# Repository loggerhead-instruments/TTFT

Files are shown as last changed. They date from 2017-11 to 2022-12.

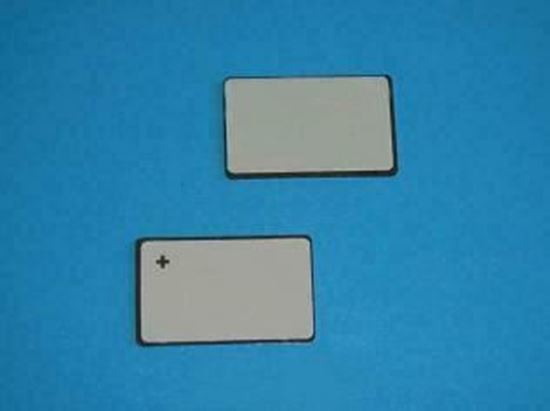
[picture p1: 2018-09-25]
spec_sheets/piezoAmp/Piezoelectric Ceramic Plate Transducer 190 KHz - SMPL131W89T10 - STEMINC_files/0001703_piezo-ceramic-plate-131x89x1mm-190-khz_550.jpeg

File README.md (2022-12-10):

# TTFT
Teeny tiny fish accelerometer tag

TTFT are miniature high-speed acceleromter data logger tags

## Altium
0. TTFT: AtMega328p high-speed accelerometer tag running at 3.0V. No real-time clock.
1. TTFT_3.0: AtMega328p development board designed to run at 3.0V
2. TTFT_3.0_tiny: AtMega328p high-speed accelerometer tag running at 3.0V. No real-time clock. No crystal for AtMega328p (to make smaller).
3. TTFT_1.8: AtMega328p high-speed accelerometer tag with 1.8V regulator to run accelerometer at lower voltage. No real-time clock.
4. TTFT2: ATSAMD21GA high-speed accelerometer tag with real-time clock. Supports MS5837 depth and temperature sensor. Magnetic switch.
5. TTFT3: ATSAMD21GA high-speed accelerometer tag with real-time clock. Supports MS5837 depth and temperature sensor. Magnetic switch. Adds pinger circuit.

## Arduino
Firmware for TTFT tags

## spec_sheets
Technical specification sheets for TTFT tag components.

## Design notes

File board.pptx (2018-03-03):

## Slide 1

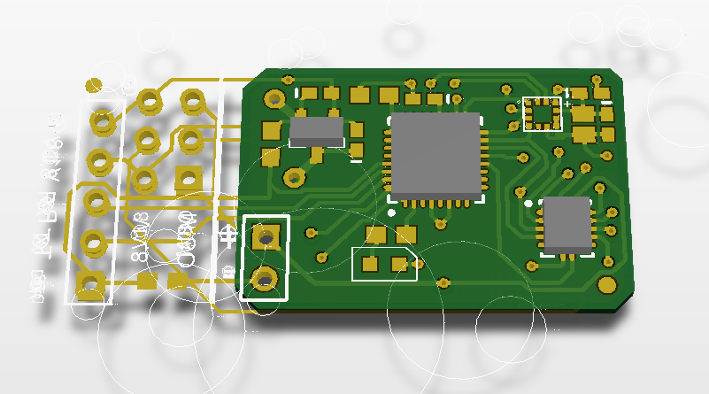
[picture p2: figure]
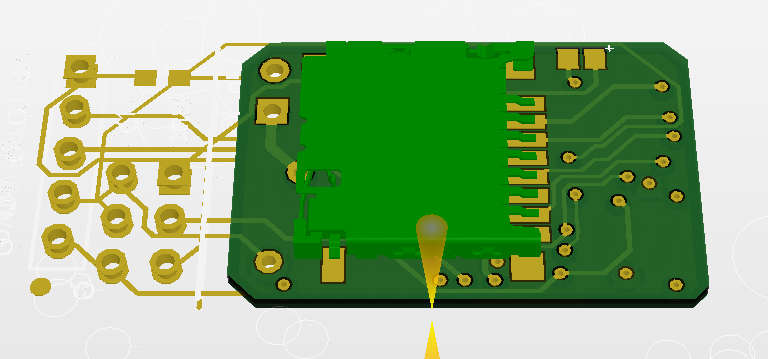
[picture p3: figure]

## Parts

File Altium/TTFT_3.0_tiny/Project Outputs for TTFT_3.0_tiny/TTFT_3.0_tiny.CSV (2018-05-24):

Bill of Material for
On 5/22/2018 at 4:47:26 PM
Comment | Manufacturer | Part number | DigiKey part number | Pattern | Quantity | Components
0.1uF | Any |  |  | 402 | 1 | C3 | Ceramic Chip Capacitor - Standard
1.0uF | Any |  |  | 402 | 2 | C8, C9 | Ceramic Chip Capacitor - Standard
100nF | Any |  |  | 402 | 2 | C5, C7 | Ceramic Chip Capacitor - Standard
10k | Any |  |  | 3-0603 | 1 | R1 | Precision Thick Film Chip Resistor, 10 Ohm to 1M Ohm Range, 1% and 0.5% Tolerance, 0603 Size, 0.063 W
10uF | Any |  |  | 805 | 1 | C6 | Tantalum cap
330x | Any |  |  | 3-0603 | 1 | R3 | Precision Thick Film Chip Resistor, 10 Ohm to 1M Ohm Range, 1% and 0.5% Tolerance, 0603 Size, 0.063 W
ATmega328P-MU | Microchip | ATmega328P-MU | ATMEGA328PB-MU-ND | 32M1-A_M | 1 | U1 | 8-Bit AVR Microcontroller with 8K Bytes of In-System Programmable Flash Memory
red LED_0603 | Any |  | SML-D12V1WT86TR-ND | Diode0603 | 1 | D1
Level Shifter | NXP | NTB0104BQ,115 | 568-8404-1-ND | DHVQFN14 | 2 | U3, U5 | Voltage level translator
LIS2DS12 | STMicroelectronics | LIS2DS12TR | 497-16261-1-ND | LGA-12 | 1 | U2
1.8V LDO | Microchip | MCP1700T-1802E/TT | MCP1700T1802ETTTR-ND | SOT-23-TT3_N | 1 | U4 | Low Quiescent Current LDO, 3-Pin SOT-23, Extended Temperature, Tape and Reel
microSD Hirose push-pull | Hirose | DM3D-SF | HR1941DKR-ND | DM3D microSD | 1 | P4

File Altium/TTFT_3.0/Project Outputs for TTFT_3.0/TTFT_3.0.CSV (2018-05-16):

Bill of Material for
On 5/14/2018 at 1:20:30 PM
Comment | Pattern | Quantity | Components
0.1uF | 0402 | 1 | C3 | Ceramic Chip Capacitor - Standard
1.0uF | 0402 | 2 | C8, C9 | Ceramic Chip Capacitor - Standard
100nF | 0402 | 2 | C5, C7 | Ceramic Chip Capacitor - Standard
10k | 3-0603 | 1 | R1 | Precision Thick Film Chip Resistor, 10 Ohm to 1M Ohm Range, 1% and 0.5% Tolerance, 0603 Size, 0.063 W
10uF | Tant0805 | 2 | C4, C6
330 | 3-0603 | 1 | R3 | Precision Thick Film Chip Resistor, 10 Ohm to 1M Ohm Range, 1% and 0.5% Tolerance, 0603 Size, 0.063 W
ATmega8-16AC | 32M1-A_M | 1 | U1 | 8-Bit AVR Microcontroller with 8K Bytes of In-System Programmable Flash Memory
AVR SPI | HDR2X3 | 1 | P3 | Header, 3-Pin, Dual row
CoinCellHolder | CoinCellHolder | 1 | P24
Header 2 | HDR1X2 | 1 | P5 | Header, 2-Pin
Header 5 | HDR1X5 | 1 | P2 | Header, 5-Pin
Header 8X2A | HDR2X8_CEN | 1 | P1 | Header, 8-Pin, Dual row
LED_0603 | Diode0603 | 1 | D1
Level Shifter | DHVQFN14 | 2 | U3, U5 | Voltage level translator
LIS2DS12 | LGA-12 | 1 | U2
MCP1700T-1802E/TT | SOT-23-TT3_N | 1 | U4 | Low Quiescent Current LDO, 3-Pin SOT-23, Extended Temperature, Tape and Reel
microSD Hirose | DM3D microSD | 1 | P4
omit | 3-0603 | 2 | R2, R4 | Precision Thick Film Chip Resistor, 10 Ohm to 1M Ohm Range, 1% and 0.5% Tolerance, 0603 Size, 0.063 W

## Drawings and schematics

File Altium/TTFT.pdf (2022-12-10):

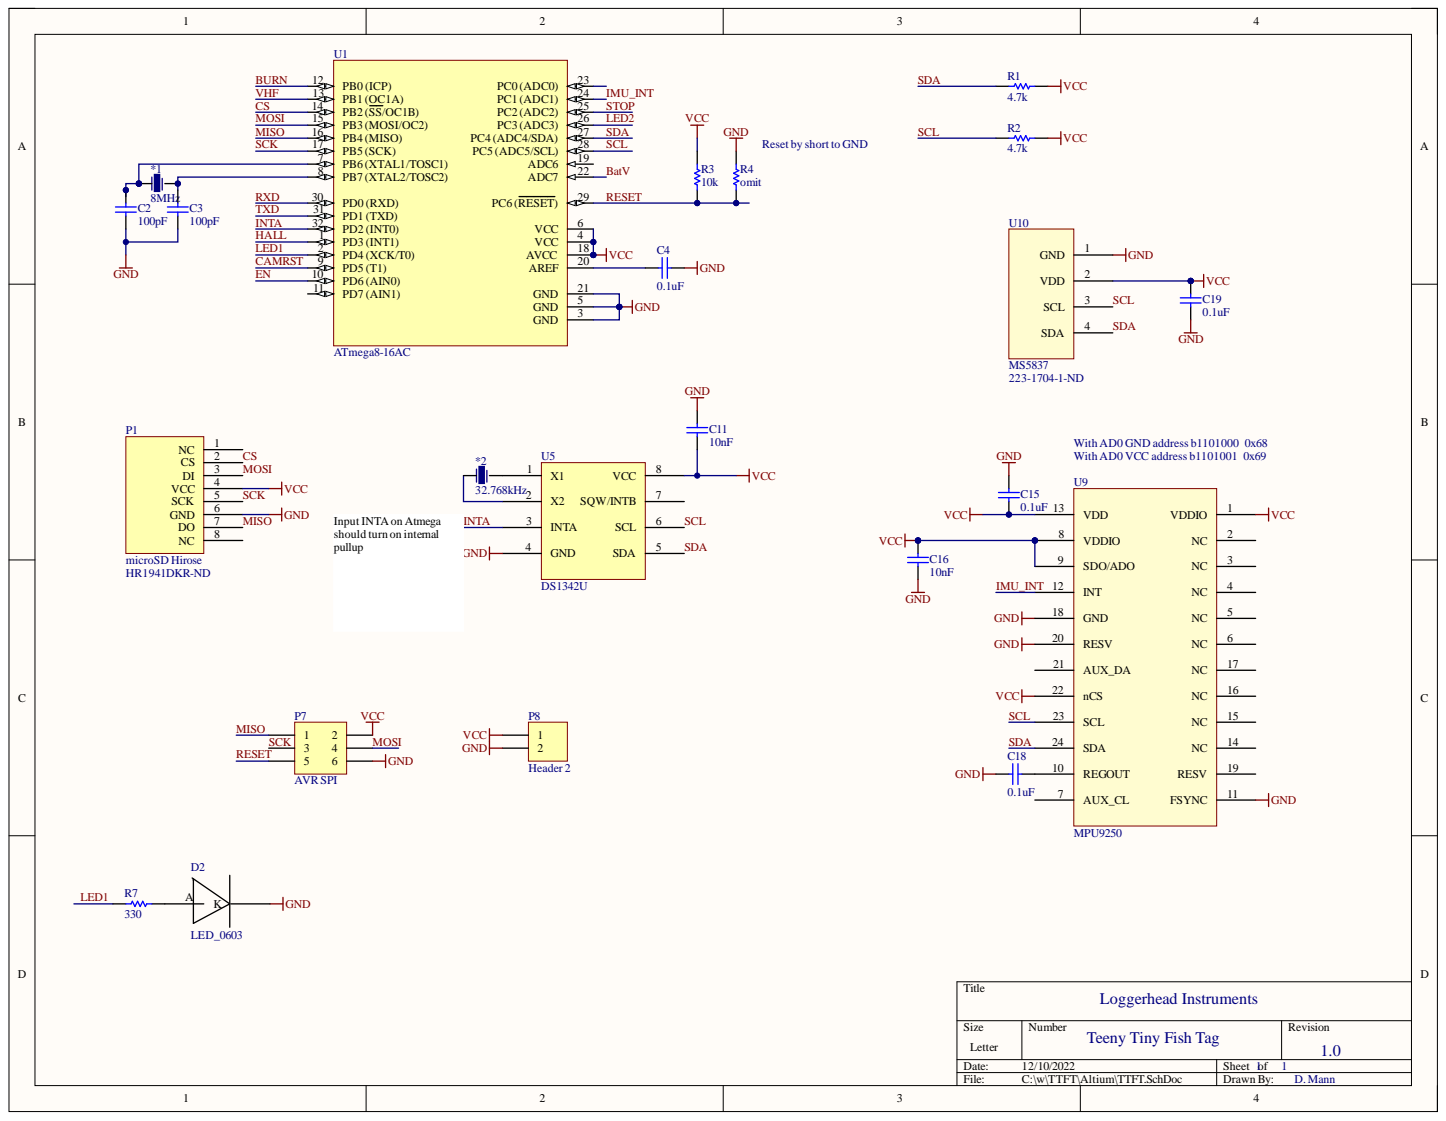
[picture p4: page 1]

Reset by short to GND

InputINTAon Atmega
should turn on internal
pullup

Teeny Tiny Fish Tag

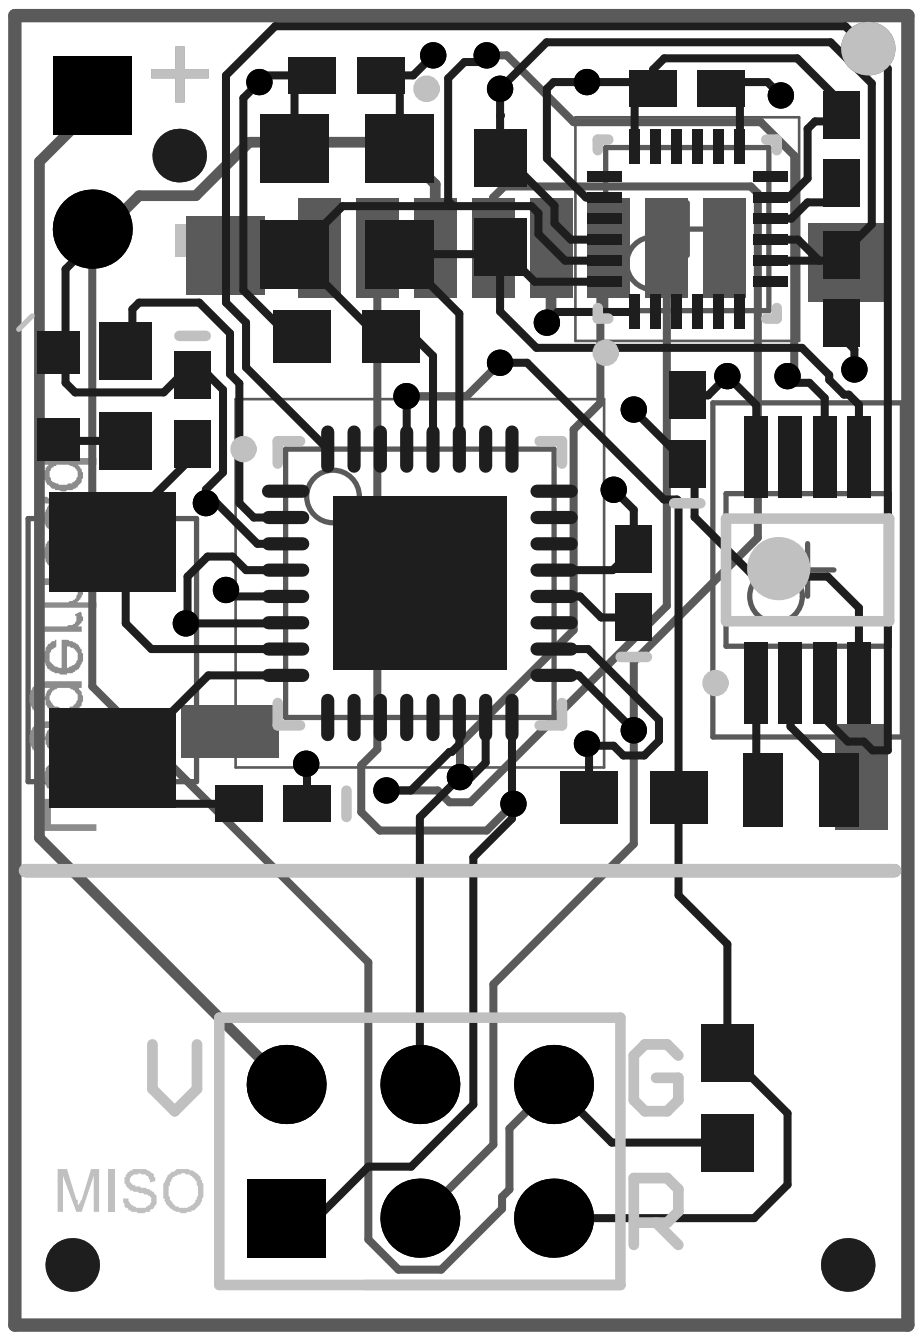
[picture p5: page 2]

Comment | Description | Designator | Footprint | LibRef | Quantity
8MHz | | *1 | XTAL-ABM3 | XTAL-ABM3 | 1
32.768kHz | | *2 | XTAL-ABS06 | XTAL_ABS06 | 1
100pF | Ceramic Chip Capacitor - Standard | C2, C3 | 0402 | C0402 | 2
0.1uF | Ceramic Chip Capacitor - Standard | C4, C15, C18, C19 | 0402 | C0402 | 4
10nF | Ceramic Chip Capacitor - Standard | C11, C16 | 0402 | C0402 | 2
LED_0603 | | D2 | Diode0603 | LED_0603 | 1
microSD Hirose | | P1 | DM3D microSD | microSD Hirose | 1
AVR SPI | Header, 3-Pin, Dual row | P7 | HDR2X3 | Header 3X2 | 1
Header 2 | Header, 2-Pin | P8 | HDR1X2 | Header 2 | 1
4.7k | Precision Thick Film Chip Resistor, 10 Ohm to 1M Ohm Range, 1% and 0.5% Tolerance, 0603 Size, 0.063 W | R1, R2 | 3-0603 | ERJ3RK | 2
10k | Precision Thick Film Chip Resistor, 10 Ohm to 1M Ohm Range, 1% and 0.5% Tolerance, 0603 Size, 0.063 W | R3 | 3-0603 | ERJ3RK | 1
omit | Precision Thick Film Chip Resistor, 10 Ohm to 1M Ohm Range, 1% and 0.5% Tolerance, 0603 Size, 0.063 W | R4 | 3-0603 | ERJ3RK | 1
330 | Precision Thick Film Chip Resistor, 10 Ohm to 1M Ohm Range, 1% and 0.5% Tolerance, 0603 Size, 0.063 W | R7 | 3-0603 | ERJ3RK | 1
ATmega8-16AC | 8-Bit AVR Microcontroller with 8K Bytes of In-System Programmable Flash Memory | U1 | 32M1-A_M | ATmega8-16AC | 1
DS1342U | | U5 | uSOP8 | DS1337 | 1
MPU9250 | Invensense | U9 | MPU6500 | MPU-9250 | 1
MS5837 | Pressure/Temp | U10 | MS5837 | MS5837 | 1

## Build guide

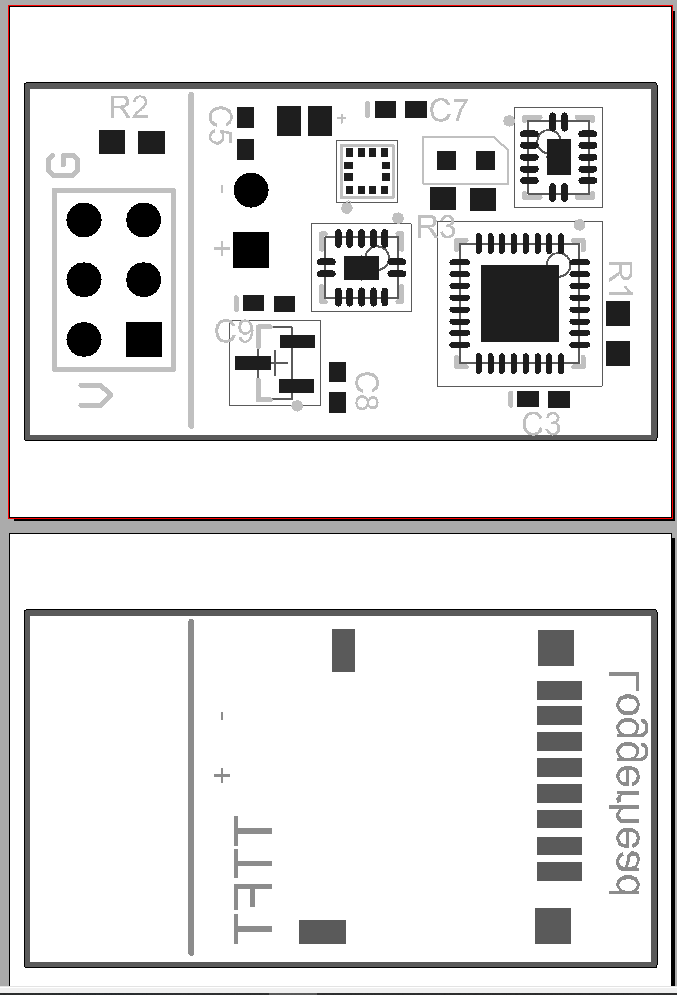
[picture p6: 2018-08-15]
Altium/TTFT_3.0_tiny/Project Outputs for TTFT_3.0_tiny/TTFT_3.0_tiny_assembly.PNG

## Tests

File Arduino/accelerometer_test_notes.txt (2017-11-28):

MPU9250
Have to use either 1000 Hz (too low) or 4000 Hz with all 3 accelerometer axes with FIFO.
No watermark

Results: Can't keep up with downloading over I2C

LIS2DS12
Has magnitude mode
256-level FIFO
14-bit
1600, 3200, 6400 Hz
If using magnitude mode, still only get 256 samples because I think it uses 3 per time slot.
watermark
Operates at a lower voltage than microSD card
150 uA at 1.8V

KX126-1063
2048-byte buffer
8 or 16-bit resolution (683 sets at low res; 342 sets at high res)
1600, 3200, 6400, 12800, 25600 data rates
watermark
145 uA at 2.5V
Confusing: Spec sheet says "Additional data can not be written to the buffer while data is being read from the buffer using auto-increment mode."
But, bullet points say can read buffer while it is being written to

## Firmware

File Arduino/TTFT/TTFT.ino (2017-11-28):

// Copyright Loggerhead Instruments, 2017
// David Mann

// TTFT is an underwater motion datalogger
// designed around the ATMEGA328p


/*
 *  RTC trigger interrupt once per second
 *  read FIFO buffer and write it
 *  check for errors on sensor init
 */


//#include <Wire.h>
#include <SPI.h>
#include <SdFat.h>
#include <MsTimer2.h> 
#include <avr/sleep.h>
#include <avr/power.h>
#include <prescaler.h>

#define SDA_PORT PORTC
#define SDA_PIN 4
#define SCL_PORT PORTC
#define SCL_PIN 5

#define I2C_TIMEOUT 100
#define I2C_FASTMODE 1

#include <SoftWire.h>
#include <avr/io.h>
#include <avr/boot.h>

SoftWire Wire = SoftWire();

//
// DEV SETTINGS
//
float codeVer = 1.00;
int printDiags = 1;

int recDur = 300;
int recInt = 0;
int LED_EN = 1; //enable green LEDs flash 1x per pressure read. Can be disabled from script.

#define MS5837_02bar // Pressure sensor. Each sensor has different constants.

#ifdef MS5837_02bar
  #define MS58xx_constant 327680.0
  #define pressAddress 0x76
#endif
#ifdef MS5837_30bar
  #define MS58xx_constant 8192.0
  #define pressAddress 0x76
#endif

// pin assignments
#define chipSelect  10
#define LED_GRN A3  // PD4
#define BURN 8     // PB0
#define VHFPOW 9   // PB1
#define BUTTON1 A2 // PC2
#define BAT_VOLTAGE A7// ADC7
#define HALL 3 // PD3 (INT1)

// SD file system
SdFat sd;
File dataFile;
int fileCount; 

int ssCounter; // used to get different sample rates from one timer based on imu_srate
byte clockprescaler=0;  //clock prescaler

//
// SENSORS
//
byte imuTempBuffer[64];
int imuSrate = 50; // must be integer for timer
int sensorSrate = 1; // must divide into imuSrate
int slowRateMultiple = imuSrate / sensorSrate;
int speriod = 1000 / imuSrate;

//Pressure and temp calibration coefficients
uint16_t PSENS; //pressure sensitivity
uint16_t POFF;  //Pressure offset
uint16_t TCSENS; //Temp coefficient of pressure sensitivity
uint16_t TCOFF; //Temp coefficient of pressure offset
uint16_t TREF;  //Ref temperature
uint16_t TEMPSENS; //Temperature sensitivity coefficient
byte Tbuff[3];
byte Pbuff[3];
volatile float depth, temperature, pressure_mbar;
boolean togglePress = 0; // flag to toggle conversion of temperature and pressure

// RGB
int16_t islRed;
int16_t islBlue;
int16_t islGreen;
int16_t accelX, accelY, accelZ;
int16_t magX, magY, magZ;
int16_t gyroX, gyroY, gyroZ;

int accel_scale = 16;

// impeller spin counter
volatile int spin;

// System Modes and Status
int mode = 0; //standby = 0; running = 1
volatile float voltage;

// Time
volatile byte second = 0;
volatile byte minute = 0;
volatile byte hour = 17;
volatile byte day = 1;
volatile byte month = 1;
volatile byte year = 17;

unsigned long t, startTime, endTime, burnTime;
int burnFlag = 0;
long burnSeconds;

void setup() {
  Serial.begin(115200);
  pinMode(LED_GRN, OUTPUT);
  pinMode(BUTTON1, INPUT_PULLUP);
  pinMode(BAT_VOLTAGE, INPUT);
  
  digitalWrite(LED_GRN,HIGH);
  pinMode(2, INPUT); //Arduino Interrupt2
  pinMode(3, INPUT); //Arduino Interrupt1

  Serial.println("TTFT");
  Wire.begin();
  
  Serial.println("Init microSD");
  // see if the card is present and can be initialized:
  while (!sd.begin(chipSelect, SPI_FULL_SPEED)) {
    Serial.println("Card failed");
    digitalWrite(LED_GRN, HIGH);
    delay(200);
    digitalWrite(LED_GRN, LOW);
    delay(100);
  }
  loadScript(); // do this early to set time
  initSensors();
  readRTC();
  Serial.print(year); Serial.print(" ");
 Serial.print(month);Serial.print(" ");
 Serial.print(day);Serial.print(" ");
 Serial.print(hour);Serial.print(" ");
 Serial.print(minute);Serial.print(" ");
 Serial.print(second);

 logFileWrite();
  
  if(burnFlag==2){
    burnTime = t + burnSeconds;
    Serial.print("Burn time set");
    Serial.println(burnTime);
  }
  if(startTime==0) startTime = t + 0; 
  Serial.print("Time:"); Serial.println(t);
  Serial.print("Start Time:"); Serial.println(startTime);
  digitalWrite(LED_GRN, LOW);

  setClockPrescaler(clockprescaler); // set clockprescaler from script file

  //setupWDT(11); // initialize and activate WDT with maximum period (~500 ms)

}

void loop() {
  while(mode==0){
    readRTC();
    Serial.print(t); Serial.print(" "); Serial.println(startTime);
    delay(1000);
    if(t >= startTime){
      endTime = startTime + recDur;
      startTime += recDur + recInt;  // this will be next start time for interval record
      fileInit();
      updateTemp();  // get first reading ready
      mode = 1;
      resetGyroFIFO();
      startInterruptTimer(1, clockprescaler);
    }
  } // mode = 0


  while(mode==1){
    // check if time to close
    if(t>=endTime){
      dataFile.close(); // close file
      if(recInt==0){  // no interval between files
        endTime += recDur;  // update end time
        fileInit();
        break;
      }
      mode = 0;
      break;
    }

    // Check if stop button pressed
    if(digitalRead(BUTTON1)==0){
      delay(10); // simple deBounce
      if(digitalRead(BUTTON1)==0){
        stopTimer();
        digitalWrite(LED_GRN, HIGH);
        dataFile.close();
        delay(30000);
        // wait 30 s to stop
        startInterruptTimer(speriod, clockprescaler);
        fileInit();
        digitalWrite(LED_GRN, LOW);
      }
    }
  } // mode = 1
  
}


void initSensors(){
// Battery Voltage
  for(int x = 0; x<10; x++){
    readVoltage();
   // Serial.println(voltage);
    delay(100);
  }

  reset_alarm();
//  Serial.println(rtcStatus());
//  for(int i=0; i<10; i++){
//    readRTC();
//    Serial.println(second);
//    delay(1000);
//  }
  // flash LED with current hour
  digitalWrite(LED_GRN, LOW);
  delay(1000);
  readRTC();
  for(int i=0; i<hour; i++){
    delay(300);
    digitalWrite(LED_GRN, HIGH);
    delay(100);
    digitalWrite(LED_GRN, LOW);
  }


  // Pressure/Temperature
  pressInit();
  for(int x=0; x<10; x++){
    updatePress();
    delay(100);
    readPress();
    updateTemp();
    delay(100);
    readTemp();
    calcPressTemp();
//    Serial.print(" press:"); Serial.print(pressure_mbar);
//    Serial.print(" depth:"); Serial.print(depth);
//    Serial.print(" temp:"); Serial.println(temperature);
  }
  
  mpuInit(1);
//  for(int i=0; i<30; i++){
//      readImu();
//      calcImu();
//      printImu();
//      delay(100);
//    }
}

void calcImu(){
      accelX = (int16_t) ((int16_t)imuTempBuffer[0] << 8 | imuTempBuffer[1]);    
      accelY = (int16_t) ((int16_t)imuTempBuffer[2] << 8 | imuTempBuffer[3]);   
      accelZ = (int16_t) ((int16_t)imuTempBuffer[4] << 8 | imuTempBuffer[5]);    
      
     // gyroTemp = (int16_t) (((int16_t)imuTempBuffer[6]) << 8 | imuTempBuffer[7]);   
     
      gyroX = (int16_t)  (((int16_t)imuTempBuffer[8] << 8) | imuTempBuffer[9]);   
      gyroY = (int16_t)  (((int16_t)imuTempBuffer[10] << 8) | imuTempBuffer[11]); 
      gyroZ = (int16_t)  (((int16_t)imuTempBuffer[12] << 8) | imuTempBuffer[13]);   
      
      magX = (int16_t)  (((int16_t)imuTempBuffer[14] << 8) | imuTempBuffer[15]);   
      magY = (int16_t)  (((int16_t)imuTempBuffer[16] << 8) | imuTempBuffer[17]);   
      magZ = (int16_t)  (((int16_t)imuTempBuffer[18] << 8) | imuTempBuffer[19]);  
}

void printImu(){
      Serial.print("a/m/g:\t");
      Serial.print(accelX); Serial.print("\t");
      Serial.print(accelY); Serial.print("\t");
      Serial.print(accelZ); Serial.print("\t");
      Serial.print(magX); Serial.print("\t");
      Serial.print(magY); Serial.print("\t");
      Serial.print(magZ); Serial.print("\t");
      Serial.print(gyroX); Serial.print("\t");
      Serial.print(gyroY); Serial.print("\t");
      Serial.println(gyroZ);
}

void fileWriteImu(){
  dataFile.print(accelX); dataFile.print(",");
  dataFile.print(accelY); dataFile.print(",");
  dataFile.print(accelZ); dataFile.print(",");
  dataFile.print(magX); dataFile.print(",");
  dataFile.print(magY); dataFile.print(",");
  dataFile.print(magZ); dataFile.print(",");
  dataFile.print(gyroX); dataFile.print(",");
  dataFile.print(gyroY); dataFile.print(",");
  dataFile.print(gyroZ);
}

void fileWriteImuFifo(){
  
}

void fileWriteSlowSensors(){
   dataFile.print(','); dataFile.print(year);  
    dataFile.print('-');
    if(month < 10) dataFile.print('0');
    dataFile.print(month);
    dataFile.print('-');
    if(day < 10) dataFile.print('0');
    dataFile.print(day);
    dataFile.print('T');
    if(hour) dataFile.print('0');
    dataFile.print(hour);
    dataFile.print(':');
   if(minute < 10) dataFile.print('0');
   dataFile.print(minute);
   dataFile.print(':');
   if(second < 10) dataFile.print('0');
   dataFile.print(second);
   dataFile.print("Z,");
    dataFile.print(','); dataFile.print(pressure_mbar);
    dataFile.print(','); dataFile.print(depth);
    dataFile.print(','); dataFile.print(temperature);
    dataFile.print(','); dataFile.print(voltage);
}

void logFileWrite()
{
   readRTC();
   
   File logFile = sd.open("log.txt", O_WRITE | O_CREAT | O_APPEND);
   logFile.print("Code version:"); logFile.println(codeVer);
   logFile.print("Serial Number: ");
   for (uint8_t i = 14; i < 24; i += 1) {
       logFile.print(boot_signature_byte_get(i), HEX);
   }
   logFile.println();
   logFile.print(year);  logFile.print("-");
   logFile.print(month); logFile.print("-");
   logFile.print(day); logFile.print("T");
   logFile.print(hour); logFile.print(":");
   logFile.print(minute); logFile.print(":");
   logFile.println(second);

   logFile.close();
}


void flatFileOpen()
{
   readRTC();
   
   dataFile = sd.open("flat.csv", O_WRITE | O_CREAT);
   dataFile.println("accelX,accelY,accelZ,magX,magY,magZ");
   SdFile::dateTimeCallback(file_date_time);
}

void fileInit()
{
   char filename[60];
   sprintf(filename,"%02d%02d%02dT%02d%02d%02d.csv", year, month, day, hour, minute, second);  //filename is DDHHMM
   dataFile = sd.open(filename, O_WRITE | O_CREAT | O_APPEND);
   while (!dataFile){
    fileCount += 1;
    sprintf(filename,"F%06d.amx",fileCount); //if can't open just use count
    dataFile = sd.open(filename, O_WRITE | O_CREAT | O_EXCL);
   // Serial.println(filename);
    delay(100);
   }
   dataFile.println("accelX,accelY,accelZ,magX,magY,magZ,gyroX,gyroY,gyroZ,date,red,green,blue,mBar,depth,temperature,spin,V");
   SdFile::dateTimeCallback(file_date_time);
   Serial.println(filename);
}

/********************************************************************
***        Master Interrupt Routine to Read Sensors               ***
********************************************************************/
void sampleSensors(void){  
    if(LED_EN) digitalWrite(LED_GRN, HIGH);
    int fifoPts = getImuFifoPts();
    
    if(fifoPts>64){
      Serial.println(fifoPts);
      readImuFifo(64);
    }
  //  fileWriteImuFifo();

//  // MS58xx start temperature conversion half-way through
//  if(togglePress){ 
//    readPress();   
//    updateTemp();
//    togglePress = 0;
//  }
//  else{
//    readTemp();
//      updatePress();  
//      togglePress = 1;
//  }
    


//  readRTC();
//  calcPressTemp(); // MS58xx pressure and temperature
//  fileWriteSlowSensors();
  ssCounter = 0;
  spin = 0; //reset spin counter
  digitalWrite(LED_GRN, LOW);
    
 //   dataFile.println();
}

//This function returns the date and time for SD card file access and modify time. One needs to call in setup() to register this callback function: SdFile::dateTimeCallback(file_date_time);
void file_date_time(uint16_t* date, uint16_t* time) 
{
  *date=FAT_DATE(year + 2000,month,day);
  *time=FAT_TIME(hour,minute,second);
}

void readVoltage(){
  voltage = analogRead(BAT_VOLTAGE) * 0.0042;
}

void startInterruptTimer(int speriod, byte clockprescaler){
    MsTimer2::set(speriod>>clockprescaler, sampleSensors); // bitshift by clockprescaler...will round if not even
    MsTimer2::start();
}

void stopTimer(){
    MsTimer2::stop();
}

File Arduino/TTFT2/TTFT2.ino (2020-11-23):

// TTFT2
// Board bootloader loaded using AtmelICE from Arduino IDE
// Board programmed using USB via Arduino Genuino Zero Native USB port using SAMD v 1.8.3

// Note: SAMD variants.h needs to have the following lines changed, otherwise SD_POW will get switched off when read USB
// C:\Users\dmann\AppData\Local\Arduino15\packages\arduino\hardware\samd\1.8.3\variants\arduino_zero\variant.h
// LEDs
//#define PIN_LED_13           PIN_A5
//#define PIN_LED_RXL          PIN_A5
//#define PIN_LED_TXL          PIN_A5
//#define PIN_LED              PIN_A5


// To Do:

// Improvements
// Duty cycle using multiple time-date vectors
// Configure programmed start and duty cycling through iTag terminal


// Optimizations (not critical):
// - set file duration from menu
// - to save power:
//       + change unused pins to INPUTS
//       + make a larger internal buffer so uSD writes are at least 512 bytes 
// - have backup wake from RTC (in case accelerometer hiccup)?
// - reset on WDT and check if write fail (would need bypass of startup menu on restart; maybe check if USB connected to enter menu)
// - brownout protection - if system reset (somehow), need to remember real time clock (?)

#include <Wire.h>
#include <SPI.h>
#include <SdFat.h>
#include <RTCZero.h>
#include "LowPower.h"

SdFat sd;
File dataFile;

// *** USER SETTINGS *********************//
int printDiags = 0;
uint32_t srate = 1600;
unsigned int fileCount = 0; 
volatile boolean introPeriod = 1;
uint32_t bufsPerFile = 750; // each buffer is 0.08 seconds; 750 buffers = 1 minute
// If 3 channel recording defined will store raw 3 axes data
// Otherwise will store magnitude of 3 channels
#define CHAN3

// desired slope threshold (A(t)-A(t-1)) 19 mg for 5 blocks of 16 samples
#define DET_THRESHOLD 311 // Detection threshold - 19[mg]/0.061 [mg/sample]
#define DET_CRIT 6        // Critical number of detected blocks
#define DET_BLOCK 16      // Number of accelerometer samples per block
boolean call = 0;
#define LED_HOLD 10;       // Keep LED activated for this many ACC buffers
int post_call_blocks = 0; // variable for counting ACC buffers
boolean turn_off;
uint32_t eT;
//****************************************//

#define CPU_HZ 48000000

// Pin Assignments
#define ledGreen A5
#define vSense A4
#define chipSelectPinAccel 5
#define chipSelectMemory 12 
#define chipSelect 10  // microSD
#define INT1 13
#define INT2 11
#define SDPOW 25 // previously PIN_LED_RXL
#define DATAOUT 23      //MOSI PB10
#define DATAIN 22       //MISO PA12
#define SPICLOCK 24     //SCK PB11
#define PWM 8

volatile int bufsRec = 0;

#define ledGreen_ON LOW
#define ledGreen_OFF HIGH

byte toggleledGreen = 1;

// when storing magnitude of acceleration watermark threshold are represented by 1Lsb = 3 samples
#define FIFO_WATERMARK (0x80) // samples 0x0C=12 0x24=36; 0x2A=42; 0x80 = 128
#define bufLength 384 // samples: 3x watermark
int16_t accel[bufLength];

uint32_t wavBufLength = bufLength;

// Pressure/Temp
#define pressAddress 0x76
float MS58xx_constant = 8192.0; // for 30 bar sensor
// float MS58xx_constant = 327680.0; // for 2 bar sensor; will switch to this if 30 bar fails to give good depth
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

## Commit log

2017-10-19 sensor init and test
2017-10-31 power in corner so fit CR2032 battery
    [TTFT.PcbDoc]
2017-10-31 final drawings
    [TTFT.PcbDoc, TTFT.PrjPCB, TTFT.SchDoc]
2018-03-02 LIS2DS12 tag
    [TTFT_LIS2DS12.PrjPCB, TTFT_LIS2DS12.SchDoc]
2018-03-02 initial layout
    [TTFT_LIS2DS12.PcbDoc, TTFT_LIS2DS12.PrjPCB, TTFT_LIS2DS12.SchDoc]
2018-03-02 Atmega 1.8V version
    Can make it smaller than running Atmega off coin cell, and may be lower power
    [TTFT_1.8.PcbDoc, TTFT_1.8.PrjPCB, TTFT_1.8.SchDoc, TTFT_LIS2DS12.PcbDoc]
2018-03-02 initial routing
    [TTFT_1.8.PcbDoc, TTFT_1.8.SchDoc]
2018-03-03 flip microSd orientation
    [TTFT_1.8.PcbDoc, TTFT_1.8.PrjPCB, TTFT_1.8.SchDoc]
2018-03-03 pin 1 silkscreen
    [TTFT_1.8.PcbDoc]
2018-03-03 files to TTFT_1.8 folder
    [TTFT_1.8.PcbDoc, TTFT_1.8.PrjPCB, TTFT_1.8.SchDoc, TTFT_LIS2DS12.PrjPCB]
2018-04-27 testing TTFT 1.8V
    Trouble connecting to TTFT
    Can't use bootloader with level shifter, so hard to troubleshoot
2018-04-27 TTFT with 3.0V on atmega
    level shifter to accelerometer
    [TTFT_3.0.PrjPCB, TTFT_3.0.SchDoc]
2018-05-16 3V board
    [TTFT_3.0.CSV, TTFT_3.0.PcbDoc, TTFT_3.0.PrjPCB]
2018-05-18 buffer bytes 3x watermark * 2x samples
2018-05-18 LED only on between files
2018-05-18 LED blink for first file
2018-05-18 high-pass filter to output
    although, it doesn't seem to change DC offset
2018-05-18 sample byte order and bitshift
    needed to fix byte order and bitshift 2 to the right, because data were 14-bit
2018-05-18 adjust sample rate to match reality
    although set to 1600 Hz, only getting module data back at 800 Hz
2018-05-22 TTFT tiny version
    [TTFT_3.0_tiny.PcbDoc, TTFT_3.0_tiny.PrjPCB, TTFT_3.0_tiny.SchDoc]
2018-05-24 small tag
    [TTFT_3.0.PrjPCB, TTFT_3.0_tiny.CSV, TTFT_3.0_tiny.PcbDoc, TTFT_3.0_tiny.PrjPCB]
2018-05-25 download FIFO after create new file
    flash led when make new file so know it is runnnig
2018-06-07 3 axis working
    but, it never goes to sleep
    Drawing about 6 mA
2018-06-07 LED off after first file
2018-06-07 added magnitude, but issue with sample rate being 800 Hz, not 1600 Hz
2018-08-15 assembly image
2018-08-15 change ODR based on srate
    1600 Hz works for storing 3 axes or magnitude
    3200 Hz works only for magnitude
2018-08-15 800 Hz magnitude module test
2018-08-15 lower power sleep and run mode
2018-08-15 lower power
    look for double tap at 25 Hz
    disable timer and spi during sleep
2018-09-18 script to set sample rate
2018-09-18 set a default sample rate and gain in case setup.txt has errors
2019-09-05 TTFT ATSAM Board
    [TTFT2.PcbDoc, TTFT2.PrjPCB, TTFT2.SchDoc]
2019-09-11 routed PCB
    [TTFT2.PcbDoc, TTFT2.PrjPCB, TTFT2.SchDoc]
2019-10-03 sleep setup after attachInterrupt
2019-10-04 flash led on new file
2019-10-04 only sleep if INT2 high; turn on LED every minute
2020-02-05 Small updates - file name and sleep
    Added single LED at reset (to help see when magnetic switch triggers reset)
    Added millisecond timing to file names
    Fixed sleep during delayed start
2020-05-26 Logger with onboard detector v0.1
    Implemented first version of onboard lobster call detection activating LED
2020-05-27 Fixed on board detector
    Still no sleep function. Detector does trigger on some impacts, too.
2020-06-25 Code used for experiments June 2020
    Features that work:
    -Delayed start using RTC wakeup
    -3D acc logging at 1600 Hz
    -Sleep between acc buffer reads
    -LED light up for 0.5s when detecting vocalization (quite sensitive)
    Need to measure:
    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
2020-07-17 fix Pressure and magnetometer location
    [TTFT3.PcbDoc, TTFT3.PrjPCB, TTFT3.SchDoc]
2020-07-18 add ping circuit
    [TTFT3.PcbDoc, TTFT3.PrjPCB, TTFT3.SchDoc]
2020-07-24 Finally fixed sleep, plus improved millis time stamp
2022-12-10 smart PDF and readme update
    [TTFT.PrjPCB, TTFT2.PcbDoc, TTFT2.PrjPCB, TTFT_1.8.PrjPCB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]
2022-12-10 smartPDF and readme update
    [TTFT2.PrjPCB, TTFT3.PrjPCB]
2022-12-10 move folders to Altium
    [TTFT2.PcbDoc, TTFT2.PrjPCB, TTFT2.SchDoc, TTFT3.PcbDoc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]
